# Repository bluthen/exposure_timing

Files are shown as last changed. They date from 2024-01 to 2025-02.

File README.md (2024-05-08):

# Exposure Timing

A lot of this project is based off New EXposure Timing Analyser (NEXTA): a GNSS-based precise timer, as presented in the wonderful paper [Reaching sub-millisecond accuracy in stellar
occultations and artificial satellites tracking](https://arxiv.org/abs/2301.06378)[arvix] ([local mirror](./nexta_2301.06378.pdf)) by authors K. Kamiński , C. Weber , A. Marciniak , M. Żołnowski & M. Gędek.

The goals are to design electronics and boards to make this easy to use.

 * PCBs that can be easily assembled, and manufactured that allow for easy LED bar registration (By having Aruco markers for example).
   * This should also make it easy to sell kits for people who do not want to solder or hand wire their own.
 * Software:
   * Binaries available for common desktop OS
   * Can automatically finds LED bar
   * Allow manually register LED bar
   * Decode each rows time
   * Generates timing info, real first exposure time, and time for any row (if rolling shutter camera). Recommends offset to be added to header/metadata. 

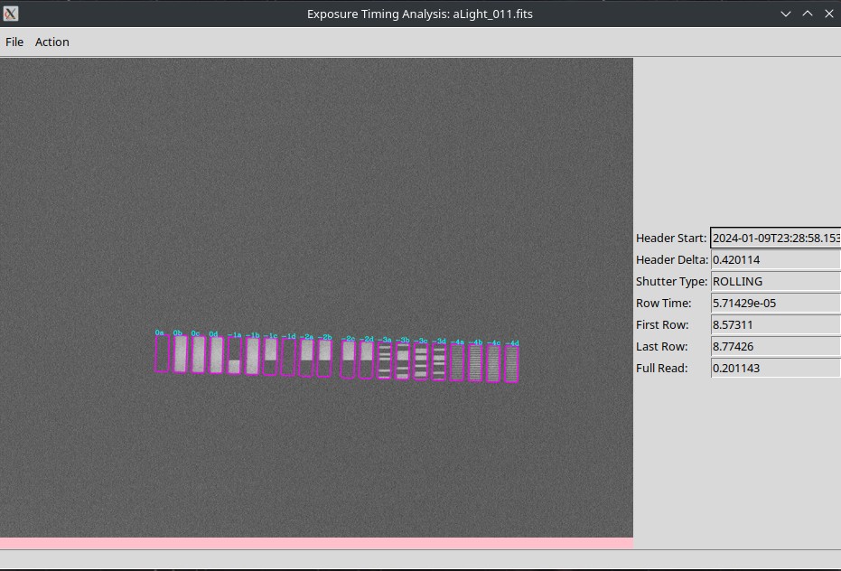
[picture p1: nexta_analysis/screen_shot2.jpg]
GUI having done time analysis

*Showing the simple GUI after time analysis has been run. Header delta is what should be added to the time stamp to make it more accurate.*

# License
Please note that individual files in the repository have different licenses. For example the NEXTA microcontroller code is under CC BY-SA 4.0 and the some of the analysis software is under the GNU GPL 3.

# Brief Description

There can be delays, or accuracy issues between when the camera is told to start it's exposure and when it actually does. This can be important for time critical applications. Also of importance is the time difference for each row in CMOS cameras with a rolling shutter.

In particular the timing application originally of interest is imaging fast time critical astronomical events. Such events include, LEO satilite, astroid transits, fast NEOs.

A better introduction is described in the paper listed above.

## Example usage

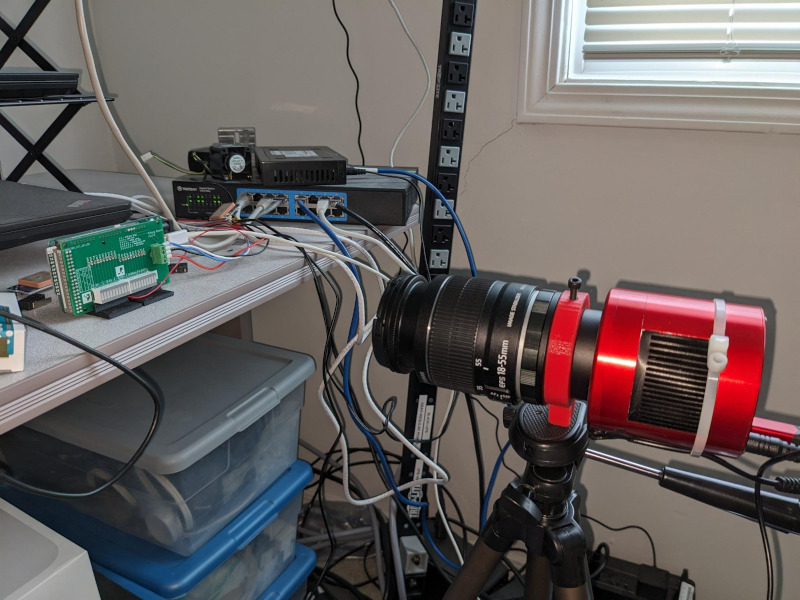
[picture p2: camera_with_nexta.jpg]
Image with camera with lens and NEXTA board


* Take your camera with a lens on it
* Put electronics (NEXTA) in front of camera, square, well focused.
* Take a intial well lit exposure used for LED bar registartion.
* After NEXTA gets GNSS lock and starts blinking, take short exposures in a dark area.
* Use analysis software to get timing info to see the difference between what is in header/metadata.

# Project contents

* [hardware](./hardware) - This includes 3d printed mount, PCB design files, and arduino firmware
* [nexta_analysis](./nexta_analysis) - Software to try to automatically decode timing images
* [nexta_html_decode_form](./nexta_html_decode_form) - A simple web form to decode the LED pattern into a time.

# Issues

There is a still a lot to do, this project is in it's early stages. Check out the [issue tracker](./issues) and, feel free to contribute.

# Instructional Videos/Purchase complete NEXTA kits

* [https://starsynctrackers.com/store/learn-nexta/](https://starsynctrackers.com/store/learn-nexta/) - Includes Arduino, assembled NEXTA Shield, GPS Moudle, GPS Antenna, Plastic Stand, and Micro USB Cable

# Other Projects

If you are interested in this project, you may be also interested in the following.

* [Project Pluto GNSS astrometry](https://www.projectpluto.com/gps_ast.htm) - Take GNSS satelites going across your frame. Since these positions are well known you can use this to get better timing (Probably up to 0.01s)

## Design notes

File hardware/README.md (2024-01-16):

# Exposure Timing Hardware

The goal here is to design PCB and other hardware to make registration and alignment easier for automatic timing analysis.

So far we have:
 * Schematics and PCB design ([KiCad](https://www.kicad.org/) and Gerbers)
 * 3d printed electronics stand ([FreeCad](https://www.freecad.org/) and STL)
 * The firmware (Arduino Sketch) provided by the authors of [Reaching sub-millisecond accuracy in stellar
   occultations and artificial satellites tracking](https://arxiv.org/abs/2301.06378)[arvix] ([local mirror](./nexta_2301.06378.pdf)) by authors K. Kamiński1 , C. Weber2 , A. Marciniak1 , M. Żołnowski3 & M. Gędek.

See the issue tracker for more work to be done.

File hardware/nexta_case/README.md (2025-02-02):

# About
This is a enclosure contributed by Vadim Nikitin, that will contain the timing board, Arduino Due, GPS/GNSS Receiver.

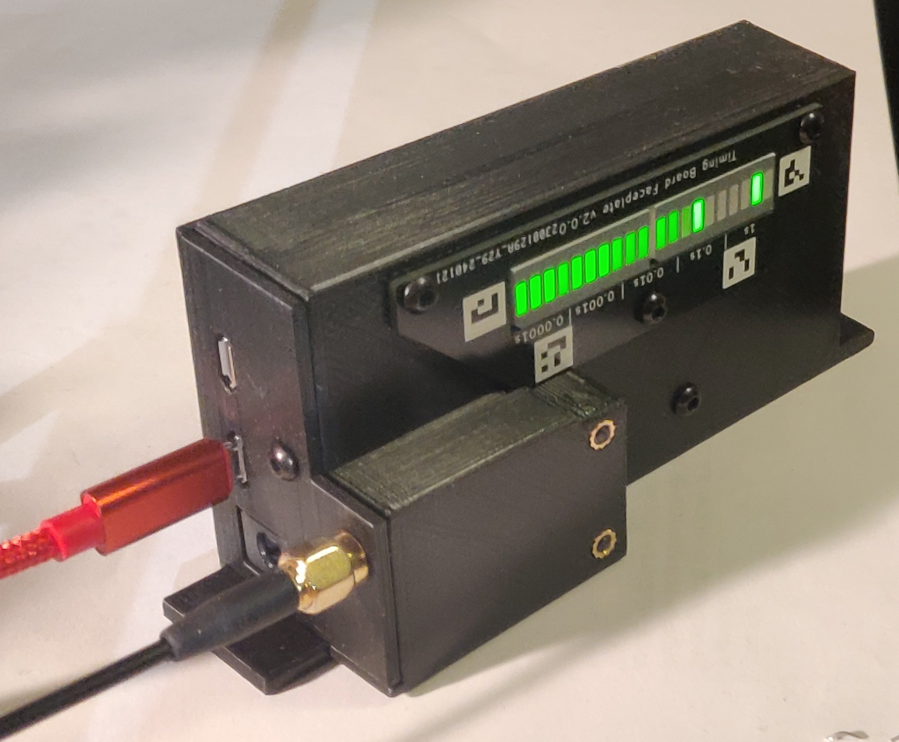
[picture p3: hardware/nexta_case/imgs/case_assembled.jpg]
Assembled enclosure and NEXTA

# Parts Needed
## Fasteners
* 6 x Ruthex M3 threaded inserts part # GE-M3x5.7-001 **see NOTE**
* 1 x M3 nut
* M3 button head screws:
  * 1 x 10 mm
  * 1 x 12 mm
  * 2 x 16 mm
  * 1 x 26 mm
  * 2 x 28 mm

**NOTE:** The case can be assembled with M3 nuts instead of inserts using 5 mm longer screws and ignoring the last 10 mm screw altogether. 

## 3D print:
* 1 x [Face](./nexta_box_v6_face.stl)
* 1 x [Lid](./nexta_box_v6_lid.stl)
* 1 x [GPS cover](./nexta_box_v6_gps_cover.stl)
* 3 x [Spacer](./nexta_box_v6_spacer.stl)

[FreeCad File](./nexta_box_v6.FCStd)

# Other
* 100mm of 5 conductor flat cable

# Assembly:
1. Unplug GPS module and Arduino board from timing board.
2. Remove screws and stands attaching face plate to the timing board. They will not be longer used.
3. Solder GPS module to the timing board using flat cable long enough to allow for further assembly (see picture).
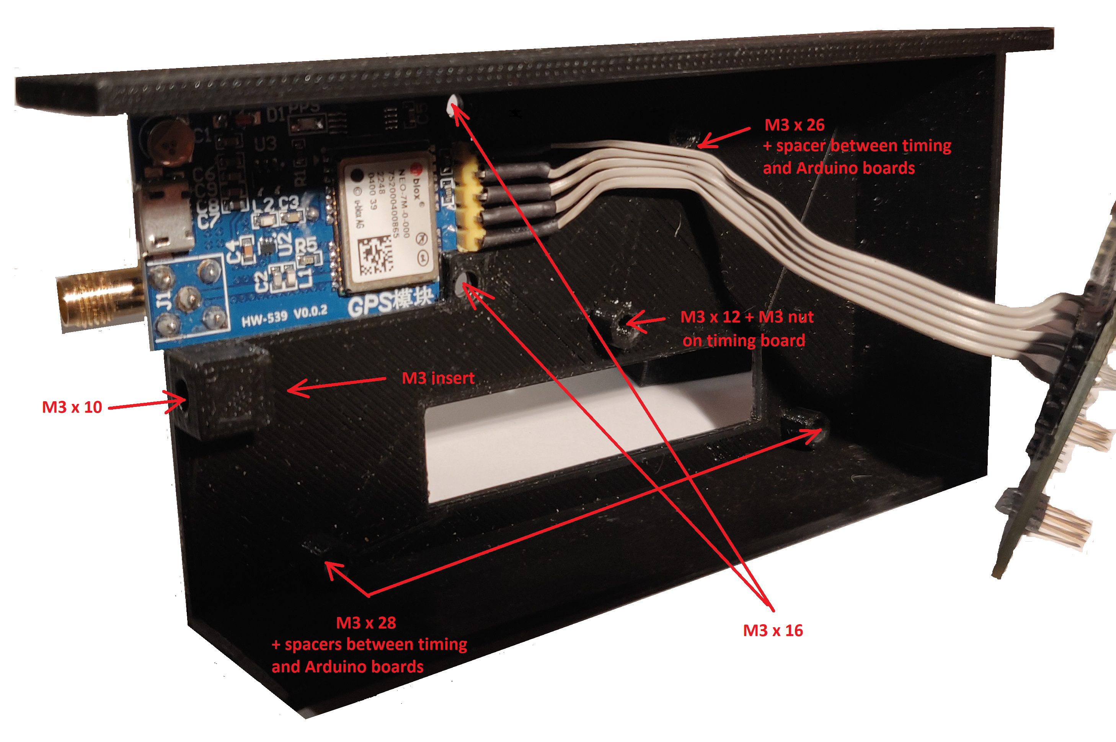
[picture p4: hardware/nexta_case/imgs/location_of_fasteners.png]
GPS modules and fastener locations
  
4. Install Ruthex inserts gently heating them with soldering iron:
  * 3 x into the Lid
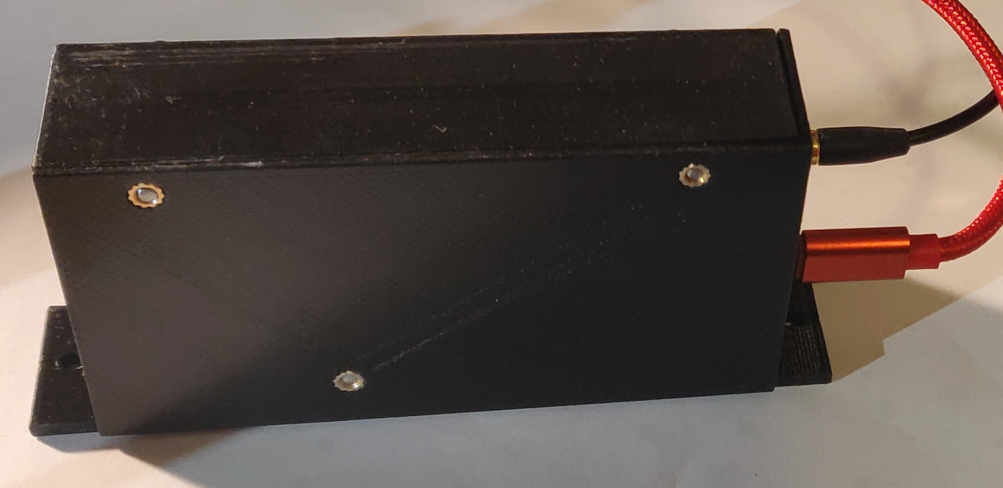
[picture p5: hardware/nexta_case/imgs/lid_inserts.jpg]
screw inserts in lid
    
  * 2 x into GPS cover
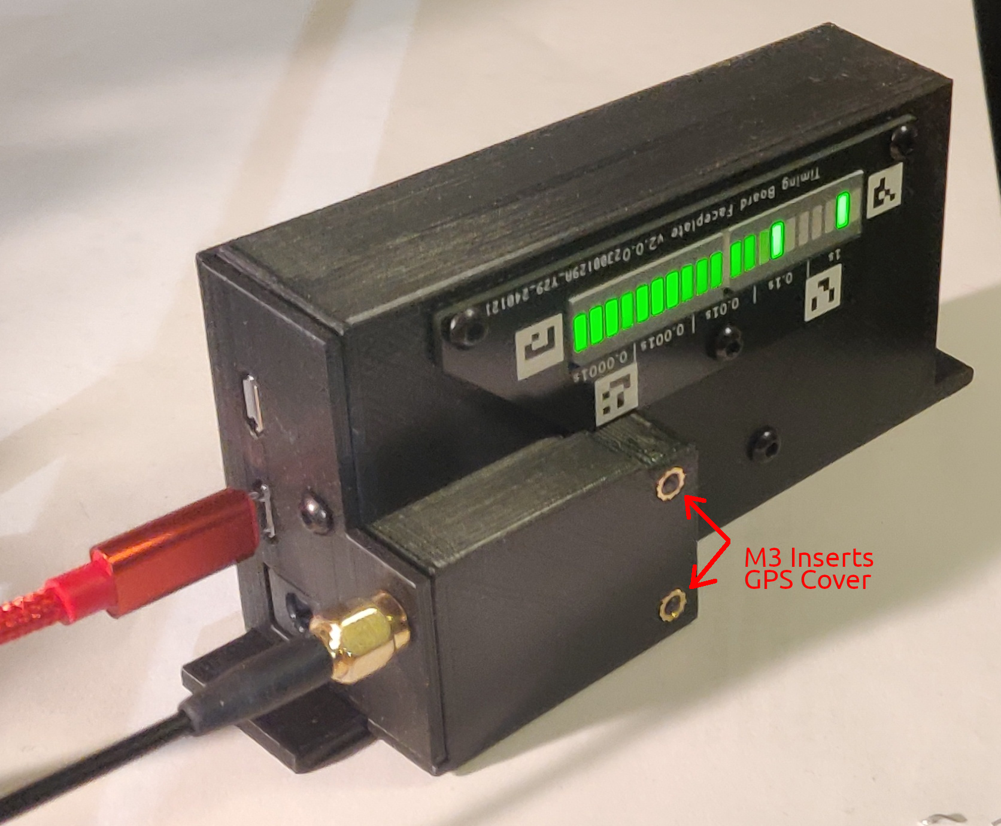
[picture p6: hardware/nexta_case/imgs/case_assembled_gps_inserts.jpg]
inserts in GPS cover
    
  * 1 x into Face part on the inside (see picture for location).
    GPS modules and fastener locations
5. Mount GPS module and cover on the outside of the Face with connector and wires inside (see picture). Screw two M3 x 16 mm screws from the inside through the holes in the Face, GPS module, and into inserts in the GPS cover.
   GPS modules and fastener locations 
6. Place timing board inside Face and faceplate outside. Make sure that flat wire clears mounting stands inside the Face. Faceplate sldes under little recess in the GPS cover. Insert M3 x 12 mm screw into middle hole of the faceplate, through Face and timing board. Fix with M3 nut to the timing board.
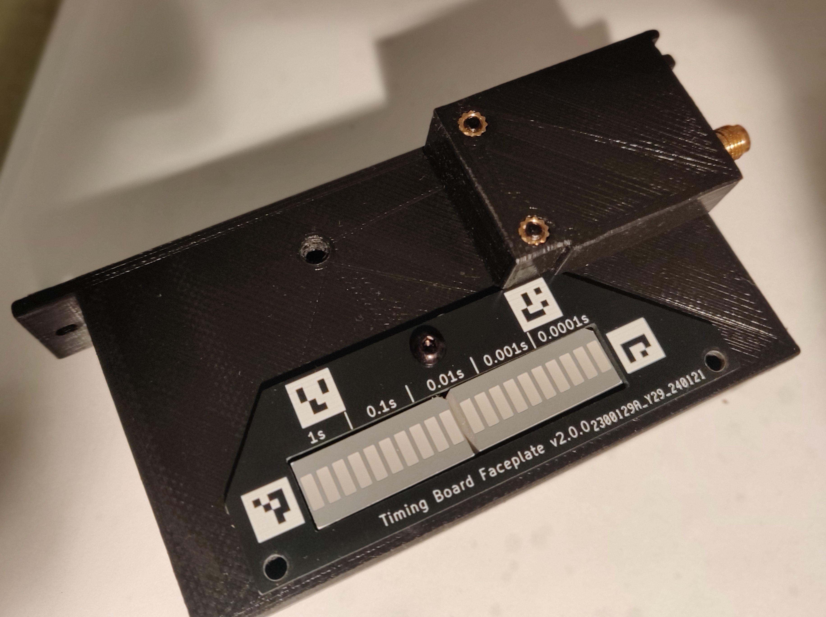
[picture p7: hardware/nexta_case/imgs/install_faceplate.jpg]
Faceplate with bolt
   
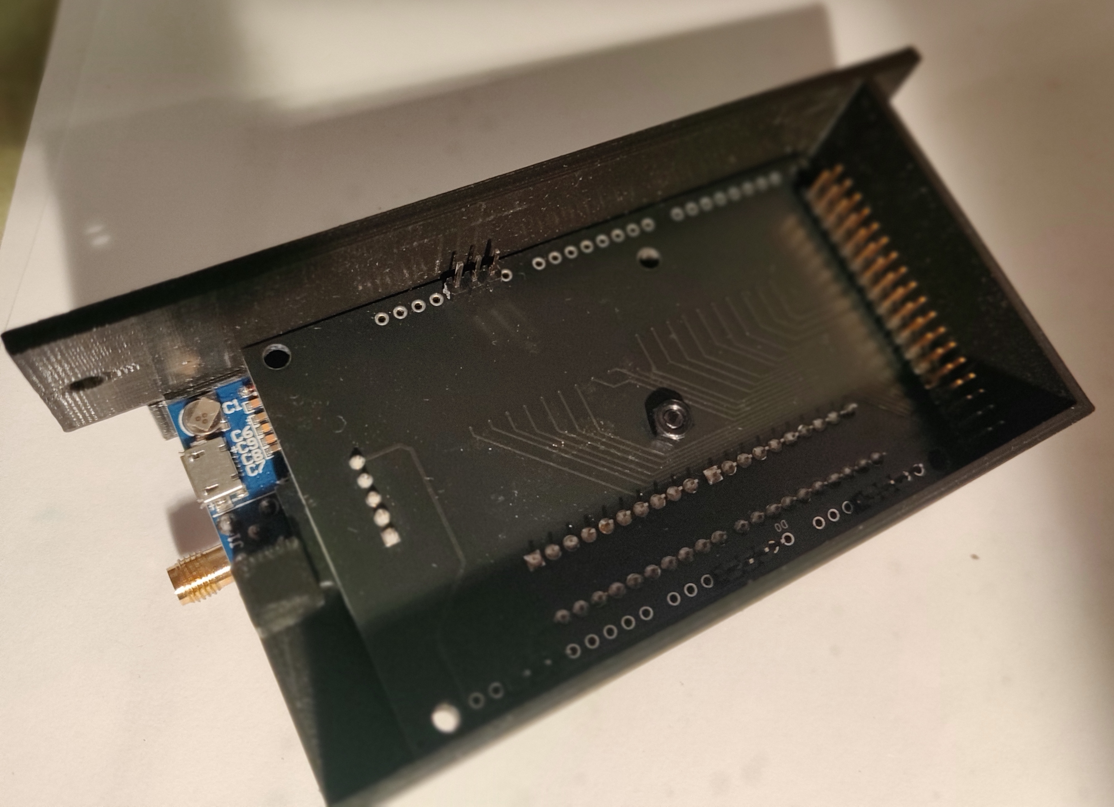
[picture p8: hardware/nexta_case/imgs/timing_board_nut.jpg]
Timing board inside face
    
7. Insert two M3 x 28 mm screws through remaining holes in the faceplate and M3 x 26 mm screw into hole in the Face. Slide three 11 mm spacers on the screws inside the Face. Carefully plug in Arduino board into the timing board. Make sure that the screws are centered in the holes of the Arduino board.
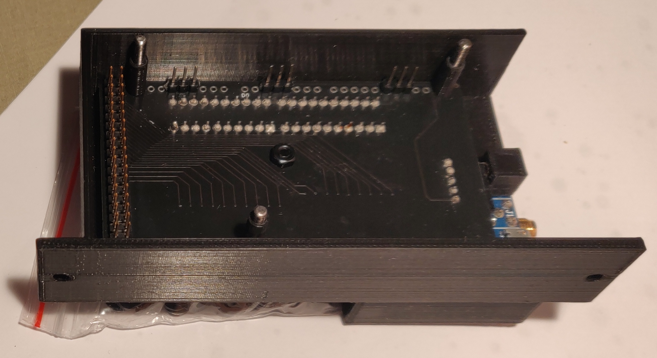
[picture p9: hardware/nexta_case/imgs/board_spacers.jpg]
Timing board spacers
   
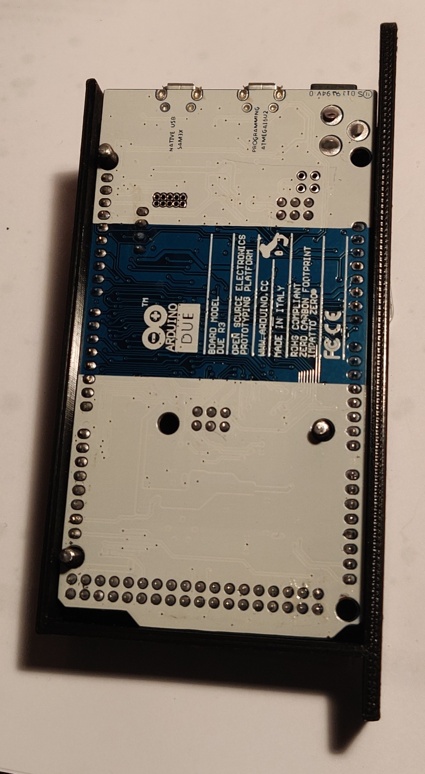
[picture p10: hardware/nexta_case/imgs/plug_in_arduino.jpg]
Arduino plugged in
    
9. Slightly pull back three screws to make ends level with Arduino board. Slide the Lid onto GPS antenna connector. Antenna connector hole in the Lid may need little cleaning to fit the connector. Keep Lid somewhat away from the Face to allow for some clearance for stands in the Lid. Slide Lid all the way. Make sure that all connectors fit into corresponding holes. Close the Lid and screw three screws into inserts in the Lid.
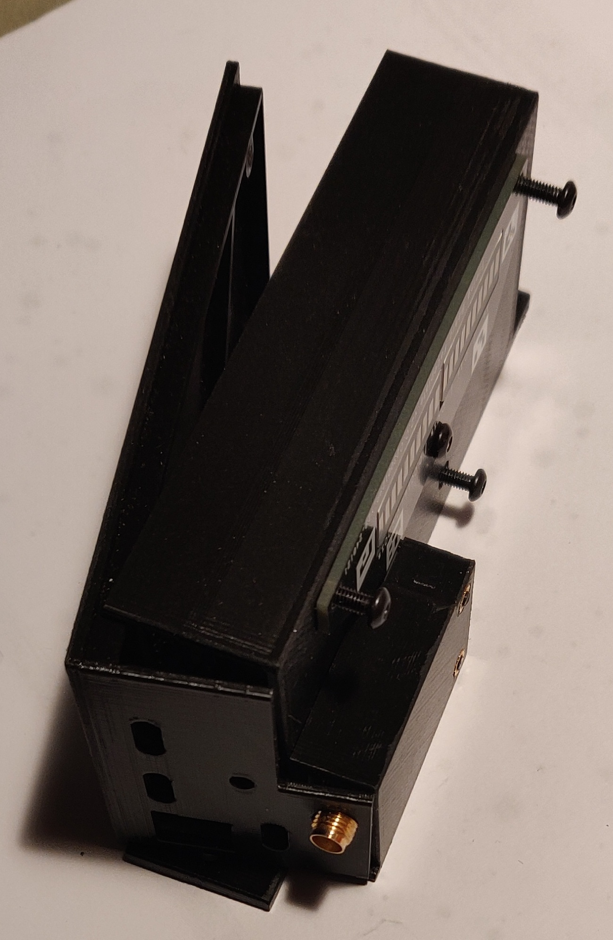
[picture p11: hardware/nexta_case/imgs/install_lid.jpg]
Install lid
   
9. Screw M3 x 10 mm screw through the hole in the connectors side of the Lid into the insert in the Face.
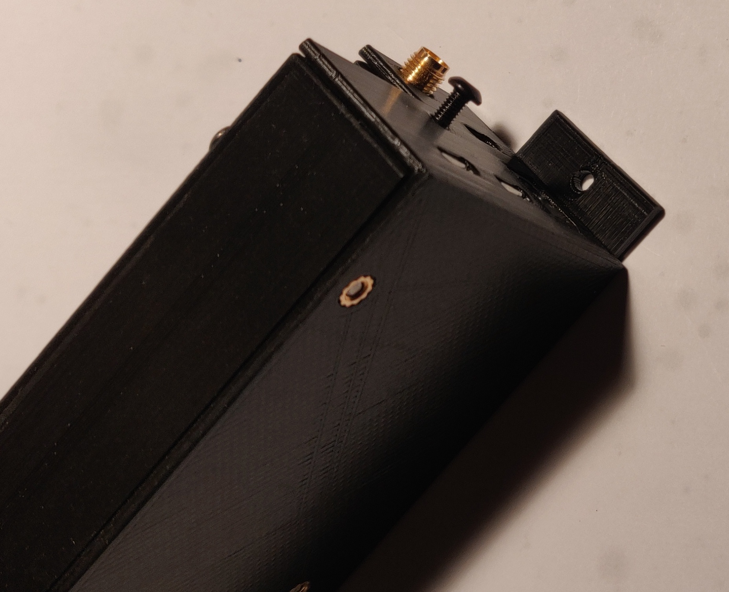
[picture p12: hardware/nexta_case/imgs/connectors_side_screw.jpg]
Connectors side lid


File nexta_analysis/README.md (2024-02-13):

# Exposure Timing - NEXTA Analysis

We try here to automate decode LED patterns into timing information.

You can use single executable binaries, or set up your own python environment to run it.

The current GUI uses tkinter.

# Quick Start

There should be binaries you can download for your desktop operating system so you don't have to set up a python
environment. A single executable that you can run. If you run it without arguments or just double click on it a GUI will
open. You can then load a registration image, register it, load a timing image and read the time. The results show on
the left.

GUI with timing info found
*Header delta is what should be added to the time stamp to make it more accurate.*

If you do have a python environment set up, you can install the dependencies with [poetry](https://python-poetry.org/).

```bash
cd nexta_analysis
poetry install
poetry shell
python read_time_gui.py
```

# Command line

Registration and analysis can be done headlessly with command line arguments. It works with both the built binary or
with python environment.

```shell
./read_time_gui registration -i ./example_files/registration_image.fits -o ./example_files/registration.etreg
```

You can then try to get timing information.

```bash
./read_time_gui readtime -r ./example_files/registration.etreg -o ./example_files/aLight_010.ettime -i ./example_files/aLight_010.fits
```

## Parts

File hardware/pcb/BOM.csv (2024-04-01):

Designator | Footprint | Comment | JLCPCB Part# | Link
R1,R2,R3,R3,R5,R6,R7,R8,R9,R10,R11,R12,R13,R14,R15,R16,R17,R18,R19,R20 | 805 | 0805 1k Ohm Resistor | C25623 | https://www.digikey.com/en/products/detail/walsin-technology-corporation/WR08X102-JTL/13240928
BAR1,BAR2 |  | LTA-1000G |  | https://www.digikey.com/en/products/detail/liteon/LTA-1000G/153278
GPS1 |  | UBLOX NEO-7M Module |  | https://www.ebay.com/sch/i.html?_from=R40&_trksid=p4432023.m570.l1313&_nkw=neo-7m&_sacat=0
Arduino Due |  |  |  | https://www.digikey.com/en/products/detail/arduino/A000062/3712582
Male Headers to connect between Arduino and PCB |  | Male .1” headers |  | https://www.digikey.com/en/products/detail/4-103327-0/A26514-40-ND/297924
GPS Antenna SMA |  |  |  | https://www.amazon.com/Bingfu-Waterproof-Navigation-Connector-Tracking/dp/B07R7RC96G/?th=1
GPS1 |  | Female .1” right angle |  | https://www.digikey.com/en/products/detail/sullins-connector-solutions/PPPC051LGBN-RC/775938

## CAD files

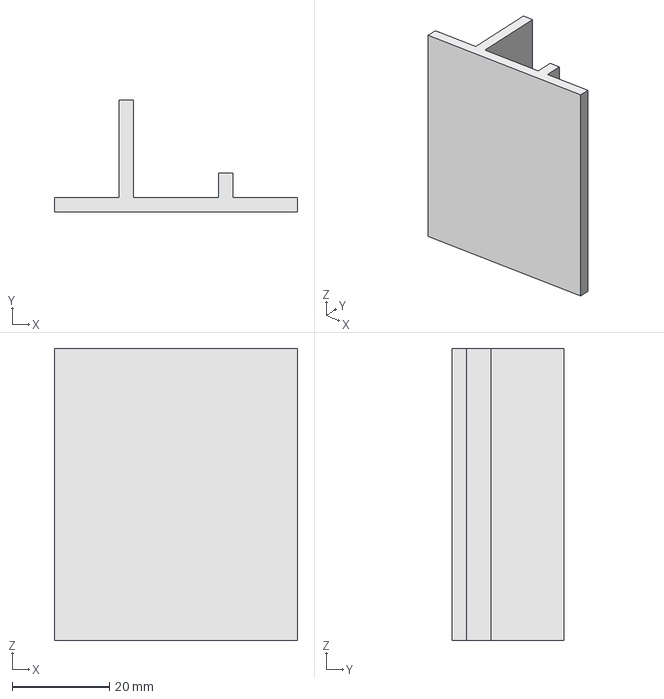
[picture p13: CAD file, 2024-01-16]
hardware/3d_stand/3d_stand.FCStd
50.0 x 23.0 x 60.0 mm

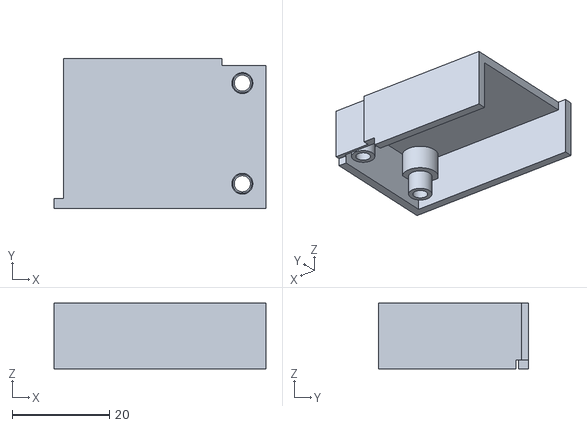
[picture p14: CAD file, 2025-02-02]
hardware/nexta_case/nexta_box_v6_gps_cover.stl
43.5 x 30.7 x 13.5

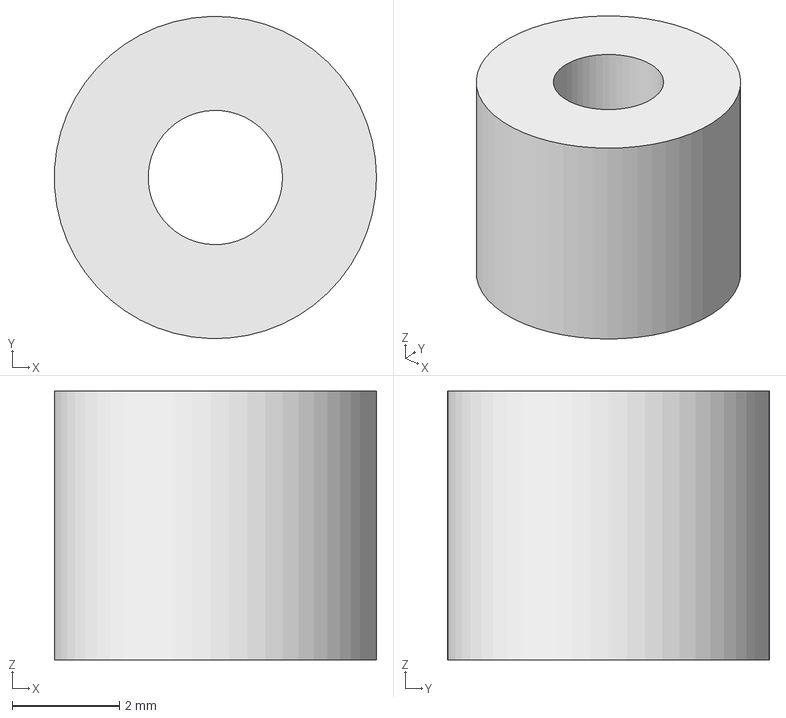
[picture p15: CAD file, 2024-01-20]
hardware/standoffs/faceplate_standoff_M3_8mm.FCStd
6.00 x 6.00 x 5.00 mm

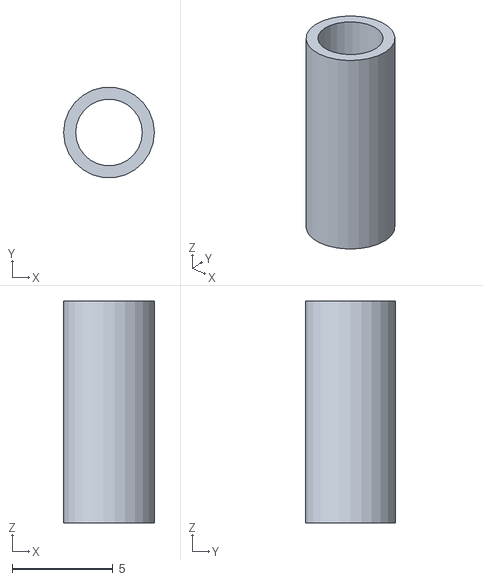
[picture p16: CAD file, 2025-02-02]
hardware/nexta_case/nexta_box_v6_spacer.stl
4.50 x 4.47 x 11.0

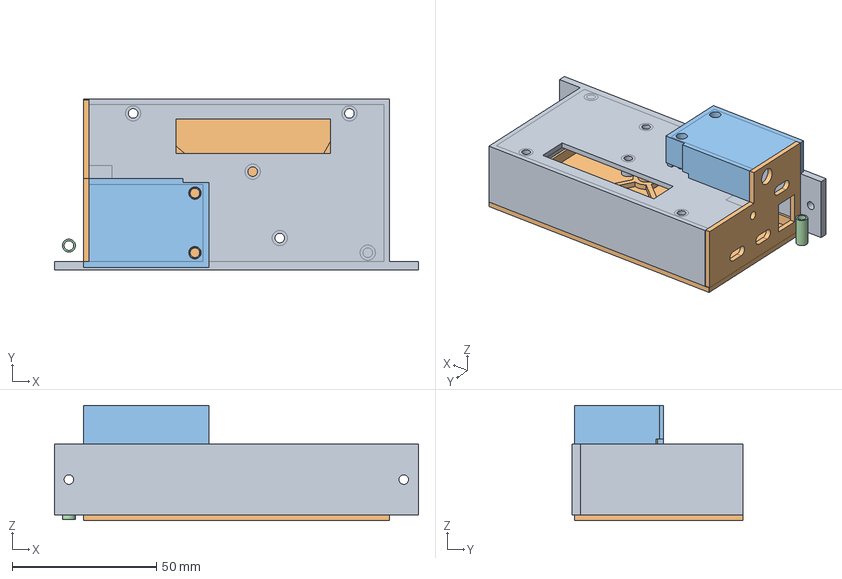
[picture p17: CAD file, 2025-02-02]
hardware/nexta_case/nexta_box_v6.FCStd
126.1 x 59.3 x 40.0 mm
lid
GpsModuleCover
spacer

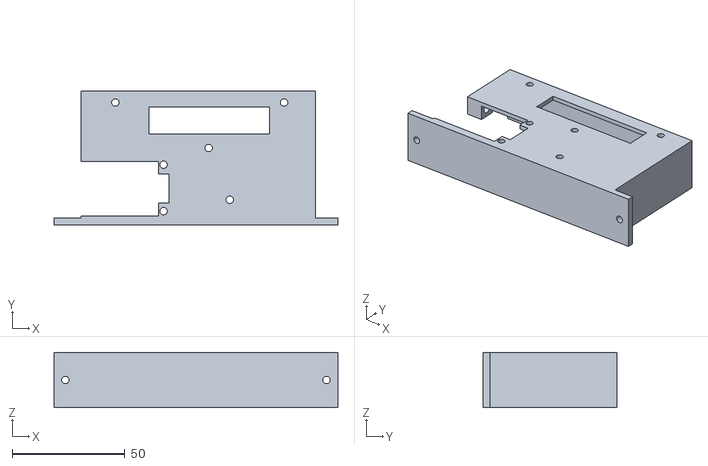
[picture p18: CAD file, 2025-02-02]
hardware/nexta_case/nexta_box_v6_face.stl
126.1 x 59.3 x 24.5

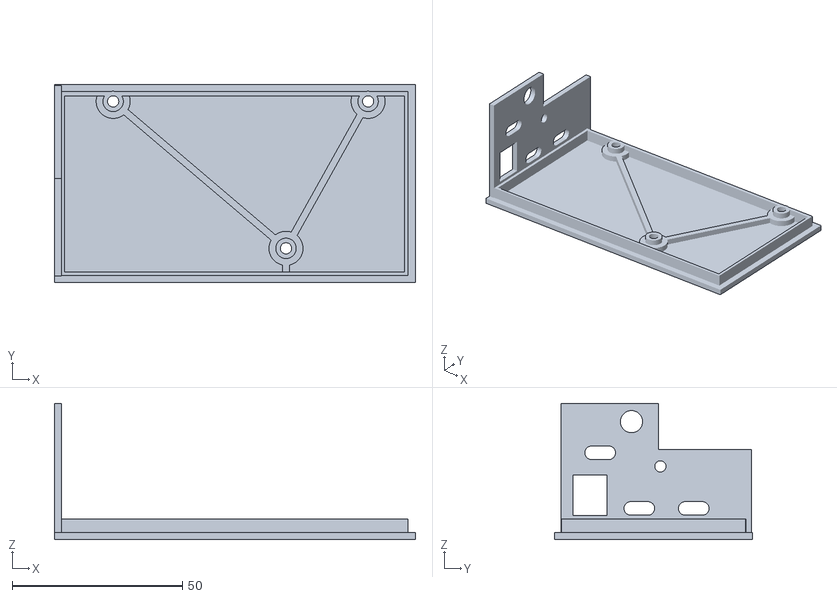
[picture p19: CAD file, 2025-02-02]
hardware/nexta_case/nexta_box_v6_lid.stl
106.1 x 58.3 x 40.0

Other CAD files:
hardware/3d_stand/3d_stand.stl
hardware/standoffs/faceplate_standoff_M3_8mm.stl

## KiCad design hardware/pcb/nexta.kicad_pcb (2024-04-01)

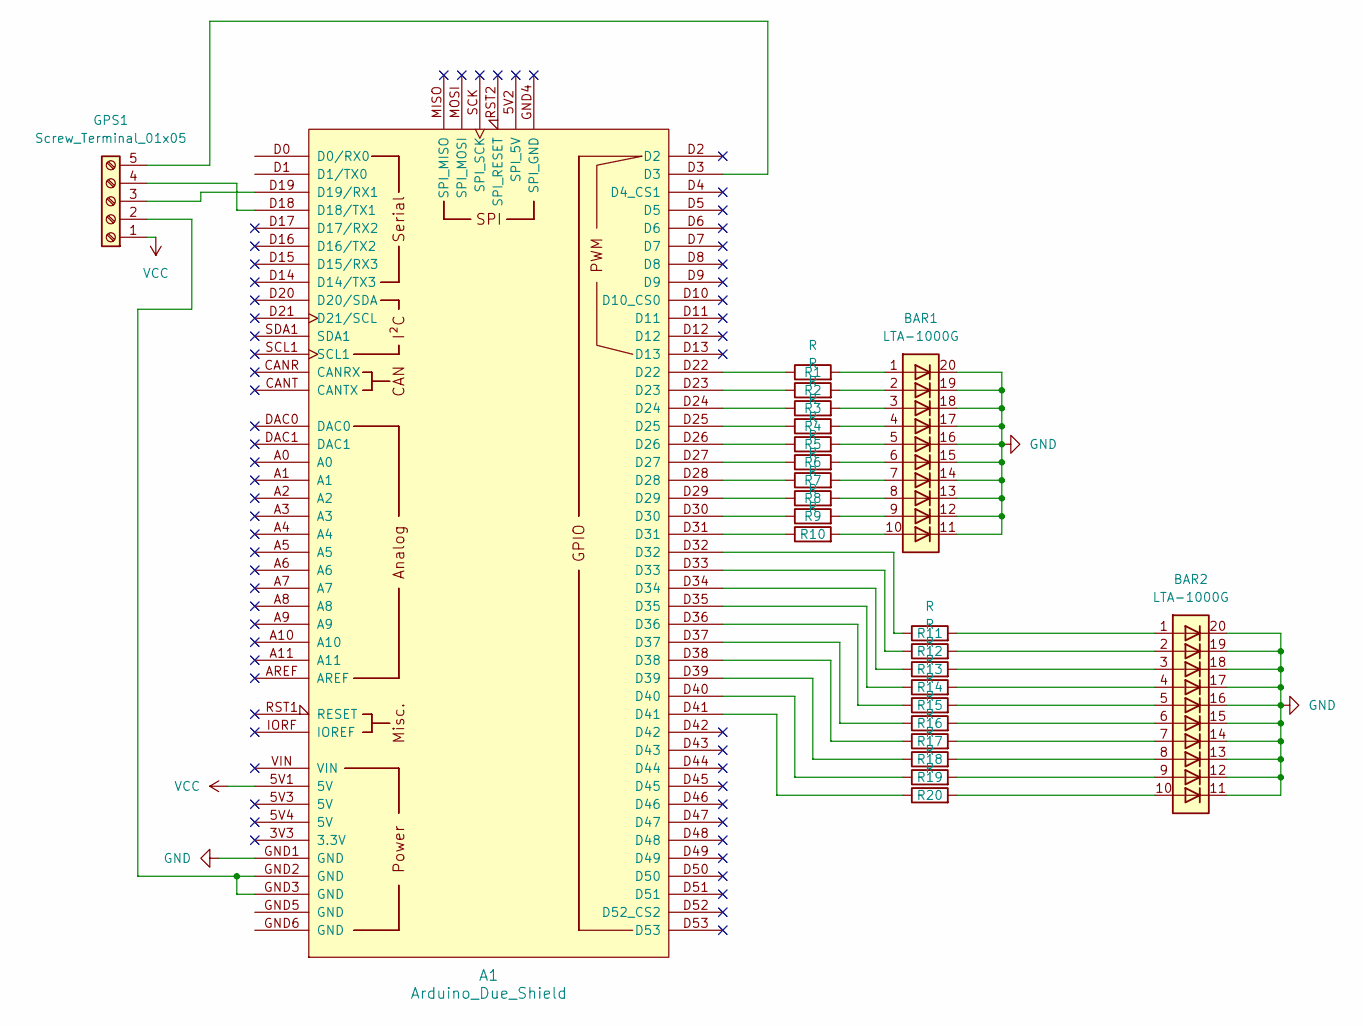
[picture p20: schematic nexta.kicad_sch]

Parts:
A1: Arduino_Due_Shield
BAR1, BAR2: LTA-1000G; HDSP-4850
GPS1: Screw_Terminal_01x05; PinHeader_1x05_P2.54mm_Vertical
R1, R2, R3, R4, R5, R6, R7, R8, R9, R10, R11, R12, R13, R14, R15, R16, R17, R18, R19, R20: R; R_0805_2012Metric

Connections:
GND: A1.GND1 (GND), BAR1.11 (K), BAR1.12 (K), BAR1.13 (K), BAR1.14 (K), BAR1.15 (K), BAR1.16 (K), BAR1.17 (K), BAR1.18 (K), BAR1.19 (K), BAR1.20 (K), BAR2.11 (K), BAR2.12 (K), BAR2.13 (K), BAR2.14 (K), BAR2.15 (K), BAR2.16 (K), BAR2.17 (K), BAR2.18 (K), BAR2.19 (K), BAR2.20 (K)
unnamed: A1.D18 (D18/TX1), GPS1.4
unnamed: A1.D19 (D19/RX1), GPS1.3
unnamed: A1.D22, R1.1
unnamed: A1.D23, R2.1
unnamed: A1.D24, R3.1
unnamed: A1.D25, R4.1
unnamed: A1.D26, R5.1
unnamed: A1.D27, R6.1
unnamed: A1.D28, R7.1
unnamed: A1.D29, R8.1
unnamed: A1.D30, R9.1
unnamed: A1.D31, R10.1
unnamed: A1.D32, R11.1
unnamed: A1.D33, R12.1
unnamed: A1.D34, R13.1
unnamed: A1.D35, R14.1
unnamed: A1.D36, R15.1
unnamed: A1.D37, R16.1
unnamed: A1.D38, R17.1
unnamed: A1.D39, R18.1
unnamed: A1.D40, R19.1
unnamed: A1.D41, R20.1
unnamed: BAR1.1 (A), R1.2
unnamed: BAR1.2 (A), R2.2
unnamed: BAR1.3 (A), R3.2
unnamed: BAR1.4 (A), R4.2
unnamed: BAR1.5 (A), R5.2
unnamed: BAR1.6 (A), R6.2
unnamed: BAR1.7 (A), R7.2
unnamed: BAR1.8 (A), R8.2
unnamed: BAR1.9 (A), R9.2
unnamed: BAR1.10 (A), R10.2
unnamed: BAR2.1 (A), R11.2
unnamed: BAR2.2 (A), R12.2
unnamed: BAR2.3 (A), R13.2
unnamed: BAR2.4 (A), R14.2
unnamed: BAR2.5 (A), R15.2
unnamed: BAR2.6 (A), R16.2
unnamed: BAR2.7 (A), R17.2
unnamed: BAR2.8 (A), R18.2
unnamed: BAR2.9 (A), R19.2
unnamed: BAR2.10 (A), R20.2
unnamed: A1.GND2 (GND), A1.GND3 (GND), GPS1.2
unnamed: A1.D3, GPS1.5
VCC: A1.5V1 (5V), GPS1.1

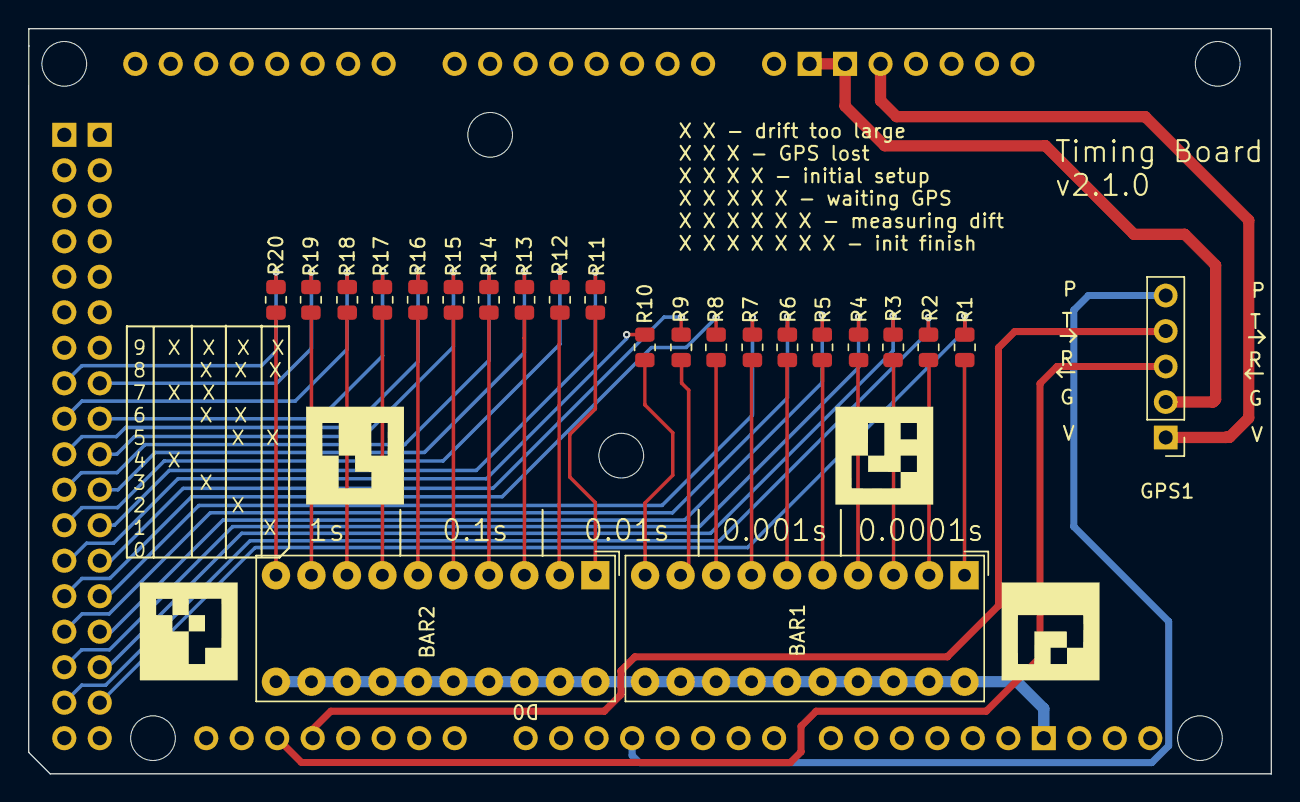
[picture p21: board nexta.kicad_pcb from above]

Board: 2 copper layers, 88.9 x 53.3 mm, 24 parts (0 on the bottom side), 46 nets.

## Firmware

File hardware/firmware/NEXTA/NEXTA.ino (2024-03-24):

//date:    2024-01-08
//author:  Krzysztof Kamiński
//email:   chrisk@amu.edu.pl
//licence: CC BY-SA 4.0
//************************************
//NEXTA - New EXposure Timing Analyser
//************************************
//hardware:
//Arduino Due
//+ Proto Shield
//+ GPS NEO 7: RX1, TX1, 0.1Hz PPS -> D3 pin, 3.3V
//+ KingBright 20 LED stripe: digital pins from 22 to 41
//software:
//Arduino IDE 1.8.19
//Arduino SAM Boards 1.6.12

#define correct_drift           //if correct_drift is defined (uncommented) than Arduino clock drift correction will be implemented at the expense of slightly longer loop time
#define GPS_wait_for_fix 1      //should NEXTA wait for fix after power up? (0-no, 1-yes)
#define GPS_wait_for_drift 1    //should NEXTA callibrate itself after power up? (0-no, 1-yes)
#define Arduino_drift_limit 10  //maximum acceptable Arduino clock drift in microsec / sec, default 10
#define GPS_pps 3               //external interrupt pin number

//calculate checksum of UBX message that is sent to GPS
void calcChecksum(byte *checksumPayload, byte payloadSize)
{
    byte CK_A = 0, CK_B = 0;
    for (int i = 0; i < payloadSize ;i++)
    {
        CK_A = CK_A + *checksumPayload;
        CK_B = CK_B + CK_A;
        checksumPayload++;
    }
    *checksumPayload = CK_A;
    checksumPayload++;
    *checksumPayload = CK_B;
}

//send message to GPS and wait for acknowledgement
//return 0 if message was sent and proper acknowledgment was received
byte getUBX_ACK(byte *msgID)
{
    byte CK_A = 0, CK_B = 0;
    byte incoming_char;
    boolean headerReceived = false;
    unsigned long ackWait = millis();
    byte ackPacket[10] = {0xB5, 0x62, 0x05, 0x01, 0x00, 0x00, 0x00, 0x00, 0x00, 0x00};
    int i = 0;
    //Serial.print(" waiting for ack...");
    while (1)
    {
        if (Serial1.available())
        {
            incoming_char = Serial1.read();
            if (incoming_char == ackPacket[i])
            {
                i++;
            }
            else if (i > 2)
            {
                ackPacket[i] = incoming_char;
                i++;
            }
        }
        if (i > 9) break;
        if ((millis() - ackWait) > 1500)
        {
            Serial.println("timeout");
            Serial.println(i);
            return 5;
        }
        if (i == 4 && ackPacket[3] == 0x00)
        {
            Serial.println("not-ack received");
            return 1;
        }
    }

    for (i = 2; i < 8 ;i++)
    {
        CK_A = CK_A + ackPacket[i];
        CK_B = CK_B + CK_A;
    }
    if (msgID[0] == ackPacket[6] && msgID[1] == ackPacket[7] && CK_A == ackPacket[8] && CK_B == ackPacket[9])
    {
        //Serial.println("ack received");
        return 0;
    }
    else
    {
        Serial.print("ack checksum failure ");
        //printlnHex(ackPacket, sizeof(ackPacket));
        delay(100);
        return 1;
    }
}

//get text form GPS - response from previously sent command
int getUBX(byte resp[], int& len)
{
    byte incoming_char;
    unsigned long ackWait = millis();
    byte start[5] = {0x00, 0x00, 0x00, 0x00, 0x00};
    int i = -1;

    //Serial.print(" waiting for response...");
    while (1)
    {
        if (Serial1.available())
        {
            incoming_char = Serial1.read();
            //Serial.print((char)incoming_char);
            if(i>=len || i>=100)
            {
                break;
            }
            if (incoming_char == 181) //0xB5
            {
                i=0;
            }
            if(i>4)
            {
                resp[i]=incoming_char;
                i++;
            }
            if(i==4)
            {
                len = incoming_char+6;

                resp[0]=start[0];
                resp[1]=start[1];
                resp[2]=start[2];
                resp[3]=start[3];
                resp[4]=incoming_char;
                i++;
            }
            if(i>=0 && i<4)
            {
                start[i] = incoming_char;
                i++;
            }
        }
        if ((millis() - ackWait) > 20)
        {
            //Serial.println("timeout.");
            //Serial.println(i);
            //Serial.print("  Response: len=");
            //Serial.print(len);
            //Serial.print(", ");
            //printlnHex(resp, len);
            return 1;
        }
    }

    //Serial.println("response received.");
    //Serial.print("  Response: len=");
    //Serial.println(len);
    //Serial.print(", ");
    //printlnHex(resp, len);
    return 0;
}

//set GPS for time functions
void setSerial()
{
    Serial.print("GPS - setting serial speed to 57600    ");
    byte message[] = {0xB5, 0x62, 0x06, 0x00,
      0x14, 0x00, //message length = 20 bytes
      0x01, 0x00, //port ID, reserved
      0x00, 0x00, //txReady disabled
      0xD0, 0x08, 0x00, 0x00, //UART mode (NEO 7 old UBX protocol version)
//      0xC0, 0x08, 0x00, 0x00, //UART mode
      0x00, 0xE1, 0x00, 0x00, //baud rate
      0x07, 0x00, //inMask (UBOX, NMEA and RTCM2 protocols enabled)
      0x03, 0x00, //outMask (UBOX, NMEA protocols enabled)
      0x00, 0x00, //bit flags (extended TX timeout disabled)
      0x00, 0x00, //reserved, reserved
      0x00, 0x00}; //empty bytes for checksum
    calcChecksum(&message[2], sizeof(message) - 4); //calculate checksum
    Serial1.write(message, sizeof(message));
    Serial1.flush();

    //getUBX_ACK(&message[2], 1); -> this does not work
    Serial.println("ok");
}

//get software and hardware version
void getVersion()
{
    Serial.print("GPS - get software version   ");
    byte message[] = {0xB5, 0x62, 0x0A, 0x04,
      0x00, 0x00, //message length = 0 bytes
      0x00, 0x00}; //empty bytes for checksum
    calcChecksum(&message[2], sizeof(message) - 4); //calculate checksum
    Serial1.write(message, sizeof(message));
    Serial1.flush();
    delay(3050);

    int len=100;
    byte resp[len];
    if( getUBX(resp, len)==0 )
    {
        Serial.println("ok");
    }
    else
    {
        Serial.println("unknown");
    }
}

//set GPS for time functions
void setRate()
{
    Serial.print("GPS - setting measurement rate 0.1Hz   ");
    byte message[] = {0xB5, 0x62, 0x06, 0x08, //command: CFG-RATE
      0x06, 0x00,  //message length = 6 bytes
      0xE8, 0x03,  //measurement rate 10000 ms  (0x64, 0x00,  //measurement rate 100 ms)
      0x01, 0x00,  //fixed = 0x01, 0x00
      0x00, 0x00,  //reference time: UTC = 0x00. 0x00 ; GPS = 0x01, 0x00   (NEO 7 old UBX protocol version)
//      0x00, 0x00,  //reference time: UTC = 0x00. 0x00 ; GPS = 0x01, 0x00
      0x00, 0x00}; //empty bytes for checksum    
    calcChecksum(&message[2], sizeof(message) - 4); //calculate checksum
    Serial1.write(message, sizeof(message));
    Serial1.flush();
    if( getUBX_ACK(&message[2])==0 )
    {
        Serial.println("ok");
    }
    else
    {
        Serial.println("error");
    }
}

//set GPS for time functions
void setSBAS()
{
    Serial.print("GPS - disable SBAS   ");
    //byte setSBAS[] = {0xB5, 0x62, 0x06, 0x16, 0x08, 0x00, 0x01, 0x03, 0x03, 0x00, 0xD1, 0xA2, 0x06, 0x00, 0x00, 0x00};
    byte setSBAS[] = {0xB5, 0x62, 0x06, 0x16, 0x08, 0x00, 0x00, 0x00, 0x03, 0x00, 0xD1, 0xA2, 0x06, 0x00, 0x00, 0x00};
    calcChecksum(&setSBAS[2], sizeof(setSBAS) - 4); //calculate checksum
    Serial1.write(setSBAS, sizeof(setSBAS));
    Serial1.flush();
    getUBX_ACK(&setSBAS[2]);
  
    //Serial.println("Current SBAS settings");
    byte getSBAS[] = {0xB5, 0x62, 0x06, 0x16, 0x00, 0x00, 0x00, 0x00};
    calcChecksum(&getSBAS[2], sizeof(getSBAS) - 4); //calculate checksum
    Serial1.write(getSBAS, sizeof(getSBAS));
    Serial1.flush();

    int len=50;
    byte resp[len];
    if( getUBX(resp, len)==0 )
    {
        if(resp[6]==0) Serial.println("ok");
        else Serial.println("error");
    }

    getUBX_ACK(&getSBAS[2]);

}

//set GPS for time functions
void setMessage()
{
    Serial.print("GPS - turn off GLL   ");
    byte setGLL[] = {0xB5, 0x62, 0x06, 0x01, 0x08, 0x00, 0xF0, 0x01, 0x00, 0x00, 0x00, 0x00, 0x00, 0x01, 0x01, 0x2B};
    Serial1.write(setGLL, sizeof(setGLL));
    Serial1.flush();
    if( getUBX_ACK(&setGLL[2]) == 0 ) Serial.println("ok");
    else  Serial.println("error");

    Serial.print("GPS - turn off GSA   ");
    byte setGSA[] = {0xB5, 0x62, 0x06, 0x01, 0x08, 0x00, 0xF0, 0x02, 0x00, 0x00, 0x00, 0x00, 0x00, 0x01, 0x02, 0x32};
    Serial1.write(setGSA, sizeof(setGSA));
    Serial1.flush();
    if( getUBX_ACK(&setGSA[2]) == 0 ) Serial.println("ok");
    else  Serial.println("error");

    Serial.print("GPS - turn off GSV   ");
    byte setGSV[] = {0xB5, 0x62, 0x06, 0x01, 0x08, 0x00, 0xF0, 0x03, 0x00, 0x00, 0x00, 0x00, 0x00, 0x01, 0x03, 0x39};
    Serial1.write(setGSV, sizeof(setGSV));
    Serial1.flush();
    if( getUBX_ACK(&setGSV[2]) == 0 ) Serial.println("ok");
    else  Serial.println("error");

    Serial.print("GPS - turn off RMC   ");
    byte setRMC[] = {0xB5, 0x62, 0x06, 0x01, 0x08, 0x00, 0xF0, 0x04, 0x00, 0x00, 0x00, 0x00, 0x00, 0x01, 0x04, 0x40};
    Serial1.write(setRMC, sizeof(setRMC));
    Serial1.flush();
    if( getUBX_ACK(&setRMC[2]) == 0 ) Serial.println("ok");
    else  Serial.println("error");

    Serial.print("GPS - turn off VTG   ");
    byte setVTG[] = {0xB5, 0x62, 0x06, 0x01, 0x08, 0x00, 0xF0, 0x05, 0x00, 0x00, 0x00, 0x00, 0x00, 0x00, 0x04, 0x46};
    Serial1.write(setVTG, sizeof(setVTG));
    Serial1.flush();
    if( getUBX_ACK(&setVTG[2]) == 0 ) Serial.println("ok");
    else  Serial.println("error");

    Serial.print("GPS - turn off GGA   ");
    byte setGGA[] = {0xB5, 0x62, 0x06, 0x01, 0x08, 0x00, 0xF0, 0x00, 0x00, 0x00, 0x00, 0x00, 0x00, 0x00, 0xFF, 0x23};
    Serial1.write(setGGA, sizeof(setGGA));
    Serial1.flush();
    if( getUBX_ACK(&setGGA[2]) == 0 ) Serial.println("ok");
    else  Serial.println("error");
}
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

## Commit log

2024-01-16 Initial commit.
    [3d_stand.FCStd, 3d_stand.stl, BOM.csv, nexta.kicad_pcb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]
2024-01-16 Added GPS antenna to bom.
    [BOM.csv]
2024-01-16 Improved rolling shutter calculation using 1ms led vertical patterns.
2024-01-20 4 Aruco markers, and faceplate.
    [faceplate.kicad_pcb, nexta.kicad_pcb]
2024-01-20 rename folder board-v1 to pcb
    [BOM.csv, faceplate.kicad_pcb, nexta.kicad_pcb, nexta.kicad_sch]
2024-01-20 Added M3 8mm standoff for faceplate.
    [faceplate_standoff_M3_8mm.FCStd, faceplate_standoff_M3_8mm.stl]
2024-01-28 LED Selector has support for v2 boards.
    [nexta.kicad_pcb]
2024-03-24 Added LED-on iterate at very beginning just to check wiring.
2024-04-01 Slight adjustment to threshold for finding leds areas. Very basic help and about added to gui.
2024-04-01 PCB 2.1.0
    [BOM.csv, nexta.kicad_pcb]
2024-05-08 Include link to buy pre assembled kits.
2025-02-02 NEXTA Enclosure created by Vadim Nikitin.
    [nexta_box_v6.FCStd, nexta_box_v6_face.stl, nexta_box_v6_gps_cover.stl, nexta_box_v6_lid.stl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]
